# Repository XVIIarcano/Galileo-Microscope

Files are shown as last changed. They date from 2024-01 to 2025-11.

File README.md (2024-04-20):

# GALILEO Modular Microscope

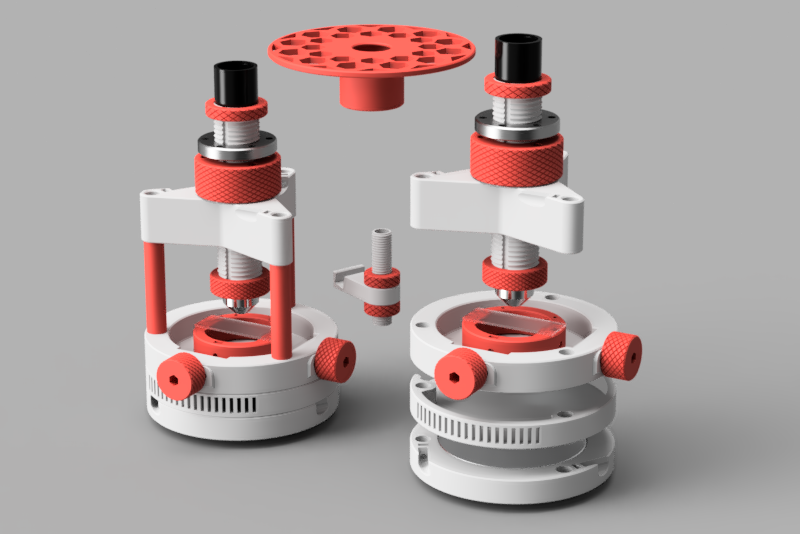
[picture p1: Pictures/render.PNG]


## Galiwhat?

This project is about an affordable, expandable and customizeable microscope based around basic hardware, 3d printing, and the few specific microscope components that cannot be worked around.
It started with a father without technical or academic knowledge whatsoever wanting to show micro-critters to his daughter, so the aim is fist and foremost to provide an enjoyable experience exploring small stuff for hobby or home use.

While Galileo is expandable, its core design prioritizes simplicity and affordability.  
I measure the success of this project on the fun you will have building it and using it, **especially** if it will be just a stepping stone for more advanced instruments and projects.

I hope to improve and expand on this project, and I would be thrilled to see other people picking up and modding it.
If you are looking for a DIY microscope already designed from the ground up to be a high end solution, with a vast selection of upgrades and configurations addressing a variety of scientific needs, have a look at the [PUMA project](https://github.com/TadPath/PUMA)

That said, it works, including the stage movement despite ample margins of improvement, and I hereby summon **The Ciliate Swarm Of Proof!**



Curious? Enthusiastic? Need to ~insult me~ _politely question my design choices_?
[**Join us on Discord**](https://discord.gg/2NHQUmsnHg)

## Basic modules

The main feature of this microscope is having each of the core functions carried out by a separate module, that exist independently and can be modded, customized and combined freely.
The basic configuration consists of the following modules and the [Printing and assembling](/Printing_and_assembling.md) file contains instructions and tips to put them together:

- **Base** 
- **Lighting (bring your own)** 
- **Stage** 
- **Standoffs**
- **Optical group** 
- **Phone holder (optional, but you will want to brag)** 

## Materials

The [BOM and components](/BOM_and_components.md) file contains a list of the necessary materials and some considerations about lenses and other accessories you will need.
I'll try to keep things synchronized but buy some extra nuts and screws ;) 

In general, you will need:

- M3 and M5 screws of different lenghts, and nuts to suit
- about 60 cm of 12 mm diameter pipe
- Some 3d printer spare parts like bed leveling springs and bowden tube.
- At least one objective, one eyepiece, and some other off the shelf microscope accessory

The objective is to keep the project lean and possibly cheap, your pricing may vary but for your reference the first functional prototype costed less than 80,00 Euros in hardware, plus the printed parts. 
Of course, if you want to bling it out you can, as with all things, but it would sort of miss the point.

## Modifications and accessories

The Mods folder is open to anyone who has something to contribute to the project.
Entries should be tested in real life, and include a readme file with any necessary information, instructions and bill of materials (don't take things for granted, remeber that this project is not meant for experts).

Simple variants, such as longer standoffs, or different tolerances on the optical tube thread, can be just generated from the CAD.
Please just notify me if you need them, I will generate them and add the STLs accordingly, no need to reinvent the wheel.

## Core specification
The core of the structure is formed by the three vertical rods of 12 mm diameter, in an equilateral triangle arrangement of 140 mm diameter (between the centers), with an external perimeter of another 10 mm all around, making the base module diameter 160 mm.
That's about it, there is no limit on how tall each "layer" should be, on the number of layers, nor on the lenght of the vertical rods, so if you have an idea for a particular lighitng setup, a finer stage module, or something else entirely, all you should do is fit it in a 160 mm diameter cylinder shape (minus the space for the rods).

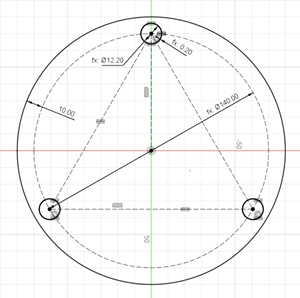
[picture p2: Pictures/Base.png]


## Wishlist and known issues

Below is a small list of things I would like to see, but have not been included in the core project (yet), if someone beats me to them, all the better!

- ~~Better movement, possibly with backlash compensation for the stage module~~ *(check the MODs folder!)*
- ~~Base alternative with some internal storage or some other solution to store stuff within the cylinder footprint when not in use~~ *(check the MODs folder!)*
- **NEW NO.1 PRIORITY** An advanced lighting module with its own light source and the possibility to mount a condenser and other amenities. *(There are some exciting developments! check the MODs folder and printables.com!)*
- ~~Fine focusing on the optical group, or a finer pitch option for the main focusing tube, or both!~~  *(check the MODs folder!)* 
- A better phone holder  

**Thanks to @MMutch on discord and @LarryD on Printables for working on their respective mods, and I hope this list can keep growing :)**

## Licensing

  
This work is licensed under a Creative Commons (4.0 International License)  
[Attribution—Noncommercial—Share Alike](https://creativecommons.org/licenses/by-nc-sa/4.0/)

## Thanks and acknowledgements

Thanks to Maff, who desinged the [Hadley telescope](https://www.printables.com/it/model/224383-astronomical-telescope-hadley-an-easy-assembly-hig) ([Metric version](https://www.printables.com/it/model/268580-hadley-telescope-official-metric-remix)).
Building and using a Hadley has been the inspiration that made me think this might be possible, and the design itself of the microscope is directly inspired by Hadley and the ecosystem of mods that grew around it.

> **Fun Fact**  
>_While I was looking for a name to this project, I found out that Italian scientist Galileo Galilei is credited with the idea of [reversing a telescope and using it as a microscope](https://en.wikipedia.org/wiki/Galileo_Galilei#Engineering), and that his first composite microscope design is [a vertical tube resting on three thin metal legs](https://catalogue.museogalileo.it/object/CompoundMicroscopeGalilean.html)... apparently the name had found me._ 

Thanks to the [Hadley discord community](https://discord.gg/DD3vHDNDjg), especially @Maff, @Baker and @Marci who encouraged me down this road after seeing the first render that was, at that point, still half a joke in my head.
They also pointed, and accompanied me, to the next chapter of my acknowledgements.

Thanks to the [Microscopy discord community](https://discord.gg/zGW95BwCy4), in particular @SmarmyNarwal and @Blekenbleu who explained many things to me without patronizing even if I was literally an incompetent barging in with ideas.
They helped me understand what I would be aiming for, what challenges I should prioritize, and how far the mark still is.

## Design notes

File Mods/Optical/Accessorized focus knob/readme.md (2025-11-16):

# Accessorized Focus Knob

_Brought to you by @Morpion on Discord and @XVIIarcano, but mostly Morpion_

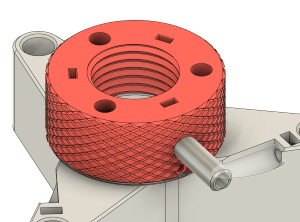
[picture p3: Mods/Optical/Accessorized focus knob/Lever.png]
/Mods/Optical/Accessorized focus knob/Lever.png

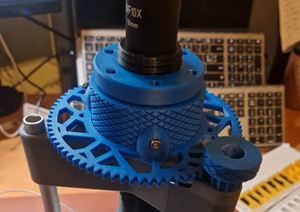
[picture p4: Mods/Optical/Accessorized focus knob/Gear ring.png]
/Mods/Optical/Accessorized focus knob/Gear ring.png


This modified knob and split ring allow the following:

- securing the knob with M3x6 screws instead of the glue 

- Attaching a lever to the knob for finer focus

- Attaching a gear ring, with a matching knob on any protruding vertical post for an even finer control

## Bill of Materials

- One set of printed parts, printed using the same settings as the rest of the microscope.

- 3x M3x6 SCHS screws for securing the knob to the split ring.
- 3x M3 nuts 
- 1x M3x30 SCHS screw for the lever.
- 3x M3x16 SHCS nuts for the gear ring.

## Assembling

- Thread the three M3x6 screws in the bottom holes around the perimeter of the knob, be gentle since you are threading on plastic. Do not tighten them all in yet.

- Drop M3 nuts in all three slots.

- Place the split ring in its seat on the spider, following the normal instructions for the anti backlash springs too.

- Position the nut and align the notches in the split ring with the screws.
Tighten the screws making sure they lock on the pockets on the split ring.
 
- Add the lever or the gear ring. 

>[!TIP]
>The rationale for the three nuts, even if you use only one lever, is that you may want to change the lever position based on where the focus point tends to fall for you, and taking the nuts out is not practical.

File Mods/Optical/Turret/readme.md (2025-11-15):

# Objective selection turret

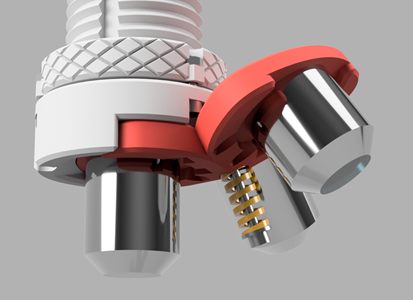
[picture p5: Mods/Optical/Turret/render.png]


This accessory replaces the standard single objective nut with a three positions rotating turret.
This way you can "zoom in" or "zoom out" selecting a different magnification objective. 

## Bill of Materials

- One set of printed parts, printed with the same settings as the rest of the microscope. You can replace the spring retainer with a simple washer, it is mostly just for show.

>[!TIP]
>Printing at a finer layer height can improve the rendering of the thread, and facilitate the assembling of the objective on the petals

- 6x M3x10 and M3 nuts (M3x12 will also work)

- 3x M3x12 SHCS screws and M3 nuts, (M3x16 will work as well, probably even M3x20 but if you go too long you start eating focuser travel)

- 1x M3x30 SHCS nut and M3 lock nut.

- 1x 8x20 mm spring (8x25 might work in combination with a longer screw)

## Assembling

Use one of your objectives to thread into the holes on the petals, then remove it, we will actually install the objectives later. The petals have RMS threads on them but it is unlikely that your printer can resolve them correctly, they will help guide the operation, but you will be actually threading the plastic with the metal of the objective. Do it nice and slow, and pay attention to go straight, and sand a bit the inner surface if needed. Take your time while the parts are disassembled, you do not want to struggle with this once the turret is on the microscope and you won't have ay leverage any more.

Assemble the rotor by joining the petals together with the M3x10 screws and nuts.

Slide the M3 lock nut in the slanted slot of the hub, note that it slides flat side down.

>[!TIP]
>The next steps are more comfortable if you remove the spider with the optical group from the microscope and keep it pointing upwards with the help of the smartphone support, just be careful not to scratch your eyepiece.

Add the gear nut to the bottom of the focusing tube, give it a couple of turns until it is out of the way.
Slide the hub in the slots of the focusing tube, careful, this will determine the orientation of the turret, I mounted mine pointing towards the bottom right, but you may prefer it pointing bottom left or even front, this is especially relevant if you also did the fine focusing lever mod, otherwise you can always just rotate the whole spider when you put it back.

When the hub teeth are level with the bottom of the optical tube, turn the ring nut back towards it, the holes on the ring nut and hub should align when there is a clearance of about 1 mm between the two.

Pass a screw trough each hole of the hub, then add the nuts in the ring nut, drawing them in until they reach the bottom of their seats, the 1 mm clearance  remains, and neither component is tilted.  
At this point the assembly is rigid, because the hub can't slide down any more, but the ring nut can't turn either.

Lean the rotor on the flat bottom of the hub, one petal flush with it.  Add the spring in the slot between the petals, and the M3x30 screw and spring retainer or washer.
Press the screw to compress the spring, then turn it to engage the lock nut and continue until it peeks out of the hole on the other side of the hub.  The locknut may have slided a bit in its seat, you can press and hold it up with a toothpick or something similar until the tip of the screw locks it in place.

Adjust the tension of the spring to your liking, it should be easy to turn, but also hold the rotor firmly enough in its three stable positions.

You can now add the objectives, and if you had removed and flipped the optical module, you can now reposition it on the microscope, checking that the objectives can rotate freely all around.
The space should be enoughto fit most objectives, but the longer ones may interfere with the thicker threaded standoff and smartphone holder or anything attached to it, so either may need to be reoriented.

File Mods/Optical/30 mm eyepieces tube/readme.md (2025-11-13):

_Originally published on printables.com by user @DaveSmith696_3620911, Discord идущийкреке_

# Description

I have redesigned the original tube (JIS), which is designed for 23.2mm eyepieces for 30mm eyepieces. The design is as simple as possible and can be modified to fit any other eyepiece, you just need to edit the CAD file to the desired size.

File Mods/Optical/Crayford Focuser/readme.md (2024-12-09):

_contributed by discord user MMutch_

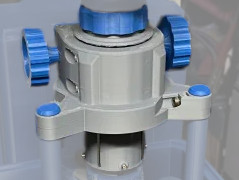
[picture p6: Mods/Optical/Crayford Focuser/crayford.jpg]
/Mods/Optical/Crayford Focuser/crayford.jpg


# Printing Instructions for the Crayford Focuser

Items marked with [a] are designated as accent, all others are primary colour.

** Print your chosen version parts I.E support vs non-support as there is a difference. **

All items have version that dont require any user added support, however there are some that ether have inbuilt removable supports or will need default slicer support adding which are only there for aesthetic reasons. Make sure that you print the corresponding parts (they are labelled in the naming structure) for example the Focuser_Body_x1 (Built in removable support).stl has a section that needs to be removed after printing where the Bearing_Block_x1 (Built in removable Support Version).stl is fitted, it should be easily removable and leave minimal signs it was there if printer/material used allows, and can be disposed of.

# BOM for Crayford Focuser

1 x Printed Parts (Body, Tube, Tube Adaptor, Eyepiece Adaptor, Bearing Block, Focus Knob, Eyepiece Locker)

3 x M5 Hex Nuts -- https://www.accu.co.uk/hexagon-nuts/7891-HPN-M5-A2

3 x M5x12 SHCS -- https://www.accu.co.uk/metric-cap-head-screws/3850-SSCF-M5-12-A2

7 x 4x3x5 Heat Set Inserts -- https://shop4fasteners.co.uk/heat-ultrasonic-threaded-inserts-brass-m3-x-5-74mm.html

7 x M3x8 SHCS -- https://www.accu.co.uk/metric-cap-head-screws/3818-SSCF-M3-8-A2

2 x M3x6 SHCS -- https://www.accu.co.uk/metric-cap-head-screws/3818-SSCF-M3-6-A2

4 x M4x20 SHCS -- https://www.accu.co.uk/metric-cap-head-screws/2830-SSC-M4-25-A2

4 x 'U' Groove 4mm x 13mm x 4mm Bearings -- https://www.amazon.co.uk/gp/product/B07V7Y1VVT/ref=ppx_yo_dt_b_search_asin_title?ie=UTF8&psc=1

1 x 110.5mm 5mm Diameter Rod (ideally Stainless steel) -- https://www.ebay.co.uk/itm/195740324799?var=495600341842&itmmeta=01HV152QP91T2EM5CFB4JQMK2A&hash=item2d930853bf:g:EbAAAOSwNFFkT~x-&itmprp=enc%3AAQAJAAAA4K%2FYtXpkaRDJxoHHHtXsM23rUVebpGkuCD9sKNMbcWPp2ZZtnkEyEJslF1Y1pCL8lxRWuFOp5TQeWT%2FXsEW4%2FUpJOw5JRbrEEODNTt2jmEa9xBe1TU9xw7Qkr7OIYFKRB4qNTfimhTiOVNK7SZk7nSfFjy3r7wZoyOf%2FKajt0uS%2FnA%2BgSC4DPSkfu%2Bp60ILHsD9mYTy%2BpDDvo%2B6V6%2FnoiL2UBgx0RtvYx8rIW7wRB%2FPS6MbpVLiF1RiyJpKAjHTR7LLsds3V4CiZFjyg8ELRTfVX8SIOEEQxq8l3zLxpU6Qy%7Ctkp%3ABFBMvPuKpdhj

2 x 16mm O/D 5mm I/D x 5mm Wide 625ZZ Bearing -- https://www.amazon.co.uk/625ZZ-Bearings-ABEC-5-Miniature-Bearing/dp/B08XLXJ6R6

2 x 109mm x 2mm Diameter Rod (ideally stainless steel) -- https://www.ebay.co.uk/itm/134173632090?itmmeta=01HV153Y9RNNQXWWSP9M3AW5Z5&hash=item1f3d5f265a:g:CSsAAOSwPc9WyGdN&itmprp=enc%3AAQAJAAAA4AygtEKGdGqWjNnNAfNLXD6kjoVY9hc1quTzC3Z7%2BIlZjWfuPSJIE8IB5LFQkUE9e4FW8ihKqvlguO6NXz8EogQujVqgYgnwSyHgwHNn8iO89YXgwOpvvCCRZDhBckjwDtcwv8xmX3V4vIzFf0%2FxNyO1piuIeUKu1ouL9RxfdqihmJRixidDZ5Qx%2FtpSkqFZ8Ae1lLsz3NLw4OVeLanNCZcGEyUbUdQRvABLeoiC95k%2B5l0AMHEaC7XXyjmuOxUKlZ06dhyhw1LMmuuJlkjScjdZCHnvAR7Xj5TuXd4wnnJS%7Ctkp%3ABFBMouWPpdhj

1 x 113mm x 10mm x 1mm Rubber Sheet -- https://www.amazon.co.uk/gp/product/B00MTW4VRA/ref=ppx_yo_dt_b_search_asin_title?ie=UTF8&psc=1

# Assembling

Body Assembly

Install the heat set inserts into the Focuser_Body_x1.stl (x4), then.

Put the 4x 'U' Groove bearings into the slots on the inside of the tube race in the Focuser_Body_x1.stl securing with the 4x M4x20 SHCS.

Focus Knob Assembly

Grind at least a 12mm flat side to the 110.5mm 5mm Diameter Rod on each end, then.

Fit one [a]_Focus_Knob_x2.stl to the 110.5mm 5mm Diameter Rod end using 1x M3x6 SHCS and slide on the 2x 16mm O/D 5mm I/D x 5mm Wide 625ZZ Bearings then fix the other [a]_Focus_Knob_x2.stl to the other end using the other M3x6 SHCS, then.

Fit the 2x 16mm O/D 5mm I/D x 5mm Wide 625ZZ Bearings with 110.5mm 5mm Diameter Rod and [a]_Focus_Knob_x2.stl into the Bearing_Block_x1.stl slots, then.

Align to the corresponding slots on the Focuser_Body_x1.stl (if using the No Support versions take not of the orientation by the direction arrow on the inside of the Bearing_Block_x1.stl) and using 4x M3x8 SHCS fix both assemblies together.

Tube Assembly

Glue (use CA glue i.e super glue) the 113mm x 10mm x 1mm Rubber Sheet to the 'flat' on the Tube_x1.stl and wait to dry, then.

Using an end of the 109mm x 2mm Diameter Rod shave off any plastic from the grooves in the Tube_x1.stl until the rods sit in the tube where the tube can smoothly without binding or any slop into the Focuser_Body_x1.stl making sure the 109mm x 2mm Diameter Rod sits in the groove of the 'U' Groove bearings, then.

Once fitting smoothly and correctly glue the rods onto the Tube_X1.stl (use CA glue i.e super glue) and wait till dry, then.

slide the Tube_x1.stl into the Focuser_Body_x1.stl

Tube to Thread Adaptor

Install the 3 x heat set inserts into the Tube_to_thread_adaptor_x1.stl, then.

Using 3 x M3x8 SHCS fix the Tube_to_thread_adaptor_x1.stl into the bottom of the Tube_x1.stl NOTE: this will lock the Tube_x1.stl into the Focuser_Body_x1.stl the screws will fit into the 3 slots on the bottom of the Focuser_Body_x1.stl when at full focus hight.

Eyepiece

Fit the stock spec eyepiece into the Eyepiece_Adaptor_x1.stl and place in the top of the Tube_x1.stl and then screw down the [a]_Eyepiece_Locker_x1.stl.

Crayford Focuser Complete

To fit to the Microscope use the stock hardware of 3 x M5x12 SHCS and 3 x M5 Hex Nuts however a modification to a tool is needed, cut down the short end of an Allen key where it fits into the head of the screw right at where the short end bends to the long end. The focuser body can be lifted to be level with the top of the stock length aluminium tubes to help with access to the samples and wont effect the function of the focuser, To which longer tube covers could be used to cover the exposed aluminium tube if desired. Also if desired there are [a]_Aluminium_Tube_Top_Caps_x3.stl's which are again purly cosmetic they have a 10.3mm O/D designed to fit 12mm O/D 11mm I/D aluminium tubes (they are a drop in fit) however if your tubes have a smalled I/D these will need sanding to fit.

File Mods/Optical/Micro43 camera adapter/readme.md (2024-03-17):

# Micro 4/3 camera adapter

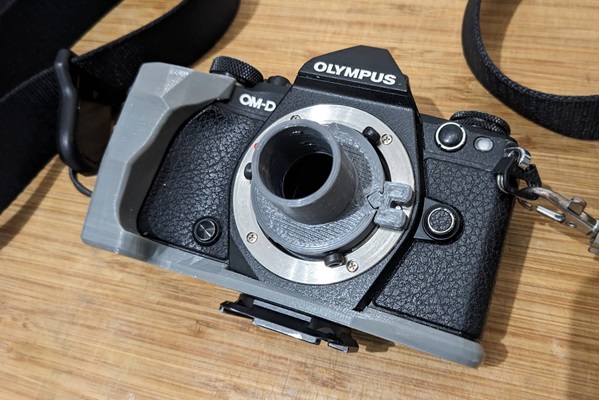
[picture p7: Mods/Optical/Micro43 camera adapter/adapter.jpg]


This adapter allows to attach a Micro 4/3 camera (tested with an OM-D E-M5 mkII) in place of the 23.2 mm eyepiece of the microscope.

For best results, enable the silent/electronic shutter with a 2 seconds delay, otherwise the kick of the mechanical shutter is enough to compromise the crispness of the image.

## Bill of Materials

- One set of printed parts, printed using the same settings as the rest of the microscope.
The block serves to latch on the lens release pin, and it is technically optional but it does help better securing the adapter.

>[!TIP]
>The fitting inside the camera body is intentionally tight, if you print it and it doesn't fit, you may have a hint of elephant foot, clean up the bottom with a deburring tool and/or sand it down a little bit.

- 3x M3x8 mm SHCS screws 

## Assembling

- Thread the three screws in the holes around the perimeter of the adapter.
Be careful as you are threading in plastic, you can stop 1 mm before the head of the screw bottoms out. 

- Push the block down in the square slot, with the flatter side of the prongs facing towards the lips of the flange, press until the top of the square plug is flush with the top of the disk. You may need to cut and file it a bit, especially if you had a bit of elephant foot, but we are going for a permanent friction fit, so if it gets stuck all the better, as soon as it goes all the way down.

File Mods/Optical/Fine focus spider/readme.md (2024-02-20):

# Fine focusing spider

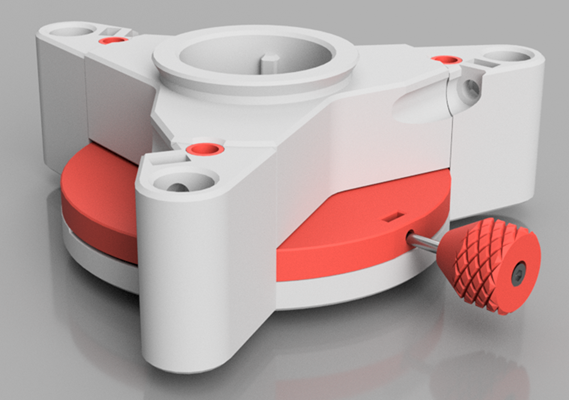
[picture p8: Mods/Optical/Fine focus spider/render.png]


This modified spider assembly allows a focuser movement of about 0.4 mm, moving the control lever over the span of about 75°.

Mechanically, this is achieved by sliding a disk with sloped surfaces in order to lift the entire main focuser mechanism by a small bit, while springs in the three corners keep the system under tension and prevent binding.  

You may also modify the CAD file to increase or decrease the slope and get a different movement range (again, within reason).  
Note that the 0.4 mm vertical movement is achieved out of the available travel of a 0.6 mm step sloping over 120°, so you may need to do some calculation to get the exact effective range you want from the 75° actual available movement.  
I also recommend adjusting in multiples of the layer height you are going to print with.

I pregenerated also a spider and rotor variant with a 1.0 mm step which should result in about 0.6 mm useful focusing range, that corresponds to 1/6th of a turn of the coarse focusing wheel using the default 3.8 mm pitch thread.   
If you do the math, you will see that we are talking about similar vertical travels over similar angles. but you may still prefer the lever control.    
I find for example that I can make smaller adjustments by grabbing the spider with the tip of my fingers and pushing forward the knob in the palm of my hand, and vice versa.

## Bill of Materials

**This mod only changes the spider of the standard focuser, please refer to the general BOM and instructions for the common parts, below is only what you will need specifically for this mod.**

- One set of printed parts, printed using the same settings as the rest of the microscope.
The "Paper Template" file is not really needed if all goes well, don't print it unless you have trouble with your PTFE tube.

- 3x 8x20 mm springs, same as those used in the standard focusing knob, but if you use longer ones they will just poke out, it may even get a steampunk vibe.

- 3x M3x40 mm SHCS screws and M3 nuts 

- 1x M3x50 mm SHCS screw, one M3 nut and optionally 1x M3 lock nut.    
>This is used as the lever shaft and can be replaced with one a bit shorter or longer. Experiment to taste considering also that you can adjust the final lever lenght by how much you will screw it in. The ideal screw is the one that sticks out the right amount for you after having bottomed out its seat in the rotor.

- 4mm diameter PTFE tube (bowden), about 55 cm for the basic version, 90 cm if you choose the PTFE lined nacelle.  
>I highlky recommend using plane cut in the slicer to print a test section of the spider, to verify the fit of your PTFE tube, if it doesn't you have a couple of options, jump to the bottom of this file.

- 3x M5x12 SHCS screws and nuts for locking the pipes (if you upgrade an existing spider you will recycle these).

>[!NOTE]
>The nacelle with PTFE groves may already improve the sliding of the disk, even if you don't actually add PTFE, as it would still have about 1/3 the contact surface.

## Assembling

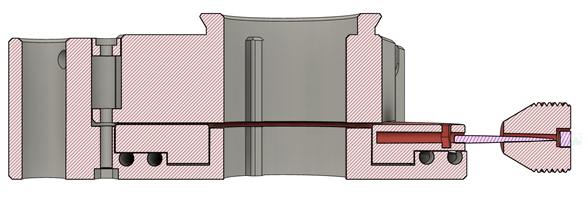
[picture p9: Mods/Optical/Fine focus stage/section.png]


- Remove the sacrificial layers from the three corners of the spider body, closing the nut slots in the bottom. Punch through them with an M3 screw and clear any burrs.

- Insert six spans of PTFE tube in the grooves of the spider body, they will provide an even slope instead of the inevitable "stairs" effect of the printed layers.   The tube should snap fit in the slot, push it one section at a time pressing down with the handle of a spoon going around the circle, cut off the excess when you get close to the end, cut as close as possible to the end of the groove, but avoid longer ends bumping and pushing out.

- Insert the M3 nut in the rotor (it goes in flat side down, unlike corner down as usual) and the M3x50 screw in the knob, then join them. As already mentioned the screw should bottom out in the pit which goes all the way trough the width of the rotor, but you can adjust it to taste or experiment with a different screw. You can also use an M3 locknut below the knob, to prevent it from sliding on the screw during use.

- If you have chosen the PTFE lined nacelle, this is the moment to insert the PTFE tubes in the bottom grooves.

- Apply grease to all mating surfaces, especially the central cylinder between rotor and spider, and the three vertical posts where nachelle and spider slide.  Place the rotor in the cradle of the spider body, followed by the nacelle. Make sure the rotor spins freely against both, and if in doubt add some grease, you can always clean up the excess once it is done.

>[!TIP]
>This is when you have to decide where you want the lever to point in relation to the microscope. Having it in front initially made sense to me but in practice I did not find it very comfortable, try placing it at the back right or back left depending on wether you are right handed or left handed, it is actually more natural as you keep your hands around the microscope, and you can control the movement by grabbing the spider and moveing the knob with the palm of your hand and vice versa.

- Drop the springs in the pits on the three corners, then the spring retainers. Use M3x40 and nuts the pits on the bottom of the spider to keep everything together. 

- Adjust the precharge of the springs, they must be just barely compressed, and they must press down evenly.  This means that unlike what appears in the render, the spring retainers may stick almost completely out, and the nut in the bottom may not engage for their full thread. If you have troubles finfing the sweetspot you may consider switching to M3x50 screws. Replacing the printed retainers with M3 washers will also shave a millimeter.      

- Proceed with the assembling of the other components and installation on the pipes, same as the standard optical module.

## PTFE whoes, and the paper trick

While putting together the prototype, I have found that the latest PTFE tube I bought was a bit larger and a bit stiffer than the one I got previously. It would not fit despite the grooves being the same dimensions as that on the bottom of the stage cart, and other projects in which the old pack of PTFE went just fine.  

Designing around all possible variations in PTFE quality is unfortunately a fool's errand, but I did make the grooves a bit more generous, since having some clearance would not be a dealbreaker in case you happen to have a smaller tube brand, while having the grooves too tight will be an issue.

If the PTFE tube you have on hand still does not fit, you have the following options.

1. Modify the CAD, there are two parameters PTFE_diameter and PTFE_poke that adjust the diameter and how much the tube rises out of the surface.

2. Try another brand, results are not guaranteed and it costs money, but it is an option.

3. The oven paper trick, weird but tested. Use the paper template file to print a donut shaped template, and use it to cut out some disks of oven paper. Stack them with some grease between spider and rotor in place of the PTFE tubes, experiment how much is enough, and how much is too much. While not ideal, oven paper does even out the printed layers and allow a smoother operation than just running the bare surfaces against each other.

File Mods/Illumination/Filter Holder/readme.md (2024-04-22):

_contributed by discord user MMutch_

This tray has a slot for standard 32 mm filters such as those available on Printables here:    
https://www.printables.com/it/model/788650-32mm-microscope-filters    
https://www.printables.com/it/model/167898-microscope-darkfield-filter-32mm    
https://www.printables.com/it/model/288750-microscope-filters

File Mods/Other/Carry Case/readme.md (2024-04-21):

_contributed by discord user MMutch_

# BOM for Carry Case

1 x Printed Parts (Base, Lid, Handle, Clips)

4 x 4x3x5 Heat Set Inserts -- https://shop4fasteners.co.uk/heat-ultrasonic-threaded-inserts-brass-m3-x-5-74mm.html

4 x M3x8 SHCS -- https://www.accu.co.uk/metric-cap-head-screws/3818-SSCF-M3-8-A2

8 x M3x30 SHCS -- https://www.accu.co.uk/metric-cap-head-screws/3818-SSCF-M3-30-A2

4 x Rubber Feet (25mm x 15mm) -- https://www.ebay.co.uk/itm/133359181553?itmmeta=01HV146RJWQ948JHB39W38KPR9&hash=item1f0cd39ef1:g:AvIAAOSwUtBjRZtq&itmprp=enc%3AAQAJAAAA4J%2FaLNfWOc3BAQ12J8P9rA3pkRGZKp1ZEXm%2FYW17OvQcGwrbzdUp9jF5NeVFmaMokFsankno6idKHbwFhG5jRMsBgvENQNQFjzV7H6iue7GSY%2F8qB3BHzD9ng4c9RjiWubMe5sBB3ophwQL3oMsIB7EFf%2FknG3xsD83HayFR%2B0quC6qYPHQTfUNtYyMq9T3v4Yt%2FyCrcDiUUSCmWRGp70heY1jJxVRUDHaetbFOHVTnZuqI1FqMOGGSHgBGcDeef6We5D0HuL2cNqpoHGIeAPWVrsfUFTxsNzfG00sPbjpAR%7Ctkp%3ABk9SR96Jm6TYYw

1 x Block of Foam (210mm x 210mm x 110mm)

# Carry Case Assembly

Fit the 4 x Rubber Feet (25mm x 15mm) to the Base_x1.stl, then.

Fit 4x M3x30 SHCS to the Base_x1.stl on the 4 sides (careful to not split the print)

Cut the Block of Foam (210mm x 210mm x 110mm) to the diameter of the microscope and fit into the base, then.

Instal the 4 x 4x3x5 Heat Set Inserts into the [a]_Handle_x1.stl, then.

Fit the [a]_Handle_x1.stl to the Lid_x1.stl using 4x M3x8 SHCS, then.

Fit the 4x [a]_Clip_x4.stl with the other 4x M3x30 SHCS to the 4 sides of the Lid_x1.stl.

Place Microscope into foam cutout and place lid over and secure with 4 side clips.

Carry Case complete.

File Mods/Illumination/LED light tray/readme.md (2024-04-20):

_Originally published on printables.com by user LarryD_

# Description

Designed this LED light to slide into the phone illumination module for the GALILEO Modular Microscope.  All of the parts were printed in Hatchbox PLA with the exception of the strain relief grommet which is PETG.  Note that the grommet will not fit unless it is printed at 69% in the X,Y directions and 100% Z direction.  I tried to make the changes in the grommet CAD file but it blows up when reduced that far.

The slide switch is wired to change between the TOP light and the BOTTOM light.  The LEDs in the parts list include a cable for USB charger and can be dimmed by holding the on/off button. 

When tightening the screws for the TOP arm tighten just enough to prevent unwanted movement so it can be repositioned easily.

I think the rest can be seen in the photos.

Parts List:

Slide Switch   
LEDs  
Double Sided Clear VHB Tape  
22 AWG Wire  
(3) M3 x 22 SHCS (for TOP Light Arm)  
(3) M3  StopNuts  
(2) M3 x 12 SHCS (for switch)  
(2) M3 Nuts  
Small Piece of plastic milk carton cut to fit opening over BOTTOM LEDs as diffuser

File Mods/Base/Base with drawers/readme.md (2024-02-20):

# Base with drawers

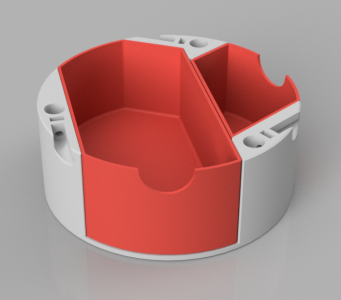
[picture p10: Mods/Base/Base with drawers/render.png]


## Bill of Materials

**This mod only replaces the design of the base module adding some internal space, screws for the rubber feet and for locking the pipes are unchanged from the standard version.**

- One set of printed parts, printed using the same settings as the rest of the microscope.  
There is an option for either the normal drawers with slots in the bottom for magnets, or simpler darwers to just print in vase mode.  

>You can use the "storage_height" parameter in the CAD file to adjust to taste, I pre-generated 60 mm and 30 mm versions. The 60 mm version is best for storing objectives, 30 mm is enough for a pack f slides, and other small items.
>There are "magnet_diameter" and "magnet_thickness" parameters as well if you happen to have a different magnet size at hand (if they are thicker than 3mm, you should also offset the bottom or you will poke a hole in it).    

- 2-6 3x8 mm magnets, each drawer has slots for 1 to 3 magnets, use as many as you prefer.  

- super glue  

## Assembling

Nothing to see here, just glue the magnets in place, add the M3 nuts for the rubber feet, slide in the rods, and secure them with the screws as for the standard base module.

>The only caveat I can think of, is that wehre on the standard base you could use longer screws for the rubber feet, and at worst you would have to cut a dent in the cover to make it fit, here a longer screw will interfere with the drawers.  
>If the correct screws are not available, you will have to cut them short or space them from below with washers or 3d printing a small buffer disk.

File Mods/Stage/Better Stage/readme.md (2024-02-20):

# Better Stage

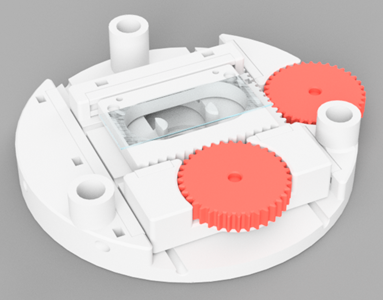
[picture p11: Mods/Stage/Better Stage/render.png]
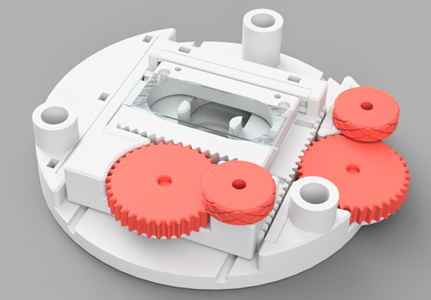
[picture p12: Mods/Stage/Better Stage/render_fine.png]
 

This mod addresses some major useability downsides with the dual M5 screw movement of the standard module.
The independent rack and pinion movement for x and y prevents the binding issue of the two interconnected knobs, and the new gears incorporate springs in order to eliminate backlash and shake inherent with the design of the basic module.

Despite being more complex, it is also easier to assemble and maintain.

> There is a basic version and a variant with fine movement knobs, if in doubt, print the latter, there is always time to remove the fine movement knobs if you change your mind, and replace them with the blank plugs which are also provided, going the other way wastes a lot of plastic.

## Bill of Materials

**This mod replaces the entire stage module, you will be able to recover only the clips and screws of the stage, therefore they are not listed in the BOM, and you may be able to recylce the PTFE tube if you can cut it and use it for the short backers without it bending out of shape**

**All screws mentioned are of the SHCS type**

- One set of printed parts, printed using the same settings as the rest of the microscope.  

- 7x M3 locknuts.

- 5x M3x10 for adjusting the rails 
> M3x12 or longer will also work, they will just stick out a bit more

- 2x M3x16 for holding the knobs

- 2x M3x20 and another 2x M3 locknuts if you use the fine movement variant.

- about 70 cm of PTFE tube

- 6x 8x20 bed leveling springs 
>unlike the anti backlash on the focuser knob, in this case 8x25 will not work
  
- super glue  

## Assembling

Remove the sacrificial layers from the following components, poking trough them with an M3 screw, and paying attention to remove any burr.

- module 
- lower plate 
- Upper half of the knobs
- Fine kobs 

Insert PTFE in all the pieces with a slot for it.  
The slots in the module and upper plate are open on the ends, meaning that the PTFE will tend to slide out, after you test fitted and cut to measure, add a few drops of superglue in the slots and press the ptfe on it so it will not budge.

Add the M3 locknuts in the slots on the module and lower plate, and M3x10 or M3x12 screws, but to not tighten them yet, give them just a couple of turns so that neither the screws nor the nuts can fall out. 

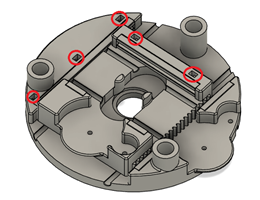
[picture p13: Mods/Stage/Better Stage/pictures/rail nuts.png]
 

Assemble the knobs by placing springs in the slots of the lower half, then leaning the upper half on it, and with the help of any flat tool (I used the back of a knife, but be safe) compress the springs so that they snap in the upper slots too.
The spring pressure should be enough to keep the two sides together. If you have troubles keeping the wheels aligned while you compress the springs, you can pass the M3x16 screw in them and a temporary M3 nut. 

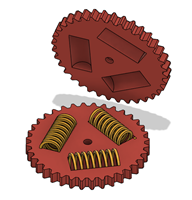
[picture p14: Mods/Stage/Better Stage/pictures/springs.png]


Prepare the upper plate by adding 2 M3x8 screws in the large holes, thread them in the plastic, until the head pokes out by a bit less than 1 mm, these will serve as stoppers for the slides, so they must be about the same height but not taller.
Install also the clips using the M3 screws and nuts that should be included with them.

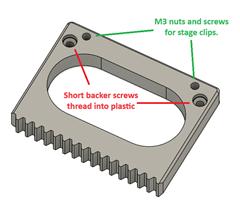
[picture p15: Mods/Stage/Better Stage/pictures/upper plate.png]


Insert the backers in the module and upper plate, they should snap fit and will be held in place by the plates, if they are loose, you can use a tiny bit of paper to shim them.
They must be level with the rack on the lower and upper plates to prevent it from tilting as the wheel moves past the centerpoint.
If you need to shim them, you should pay attention that they don't stick out too much that the wheel can't engage, nor too little that the plates can tilt.

Insert the rail in the back of the lower plate, followed by the upper plate which should slide in place freely.

Insert the lower knob in the module, aligning the teeth with the rack on the upper plate.
Secure it with the locknut on the bottom of the lower plate and the M3x16 screw.
You may add some grease on the bottom of the knob, but do not grease the teeth especially if you will use the fine focusing version, or you will get greasy fingers when you turn it. 

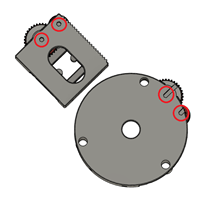
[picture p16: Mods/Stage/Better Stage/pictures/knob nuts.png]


Now it is time to tighten the screws on the back of the rail.
Start by tightening them equally until they are in contact with the rail, then by another couple of turns.
Test the sliding of the upper plate, it must move freely but with zero wobble.
Tighten and let go the screws, and the screw holding the knob, until you are happy with the results.

> [!IMPORTANT]
> Look at the plate movement from the side too, a consequence of the anti backlash split of the knobs is that the plate may tend to pull up on one side. 
> The compression applied by the screws prevents this too, and I found that the best result is achieved by keeping the side which pulls up a bit tighter than the other.

If you are assembling the fine movement version, install now the fine movement knob using the M3x20 and M3 locknut. 

>You may notice that there is a spot where the knobs and rack system runs more or less smooth due to imperfections of the print and alignment. The rack will not use one full turn of either of the knobs, so there is no harm in trying different orientations to look for the "alignment of the sweetspots".  

Install the backers and rail in the module body, folowed by the lower plate and knobs, with the same procedure and cares used for the previous stage.

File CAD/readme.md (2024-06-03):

# CAD files and resources

This folder collects useful files for the Galileo design, including the main source files for the "vanilla"  version of Galileo and a couple more, to make it easier to reference dimensions, generate derivatives, and multiple variants of certian components...

A special thanks goes to @roovian on discord for coding the [OpenSCAD file that generates standoffs with serial numbers on them](https://github.com/XVIIarcano/Galileo-Microscope/blob/main/CAD/Serial%20standoff%20generator.scad).
Use of that file is subject to the rules of the game as per the serial related channels on discord, if ou just grab it and print it, that's called cheating :P

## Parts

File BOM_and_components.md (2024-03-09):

# Bill of materials and microscope components

>[!CAUTION]
>This documentation is written by me, a salesman of totally unrelated goods with a degree in Political Sciences.  I write based on my personal experience, opinions, expectations and whatever I could understand from doing my own research.  
Some skilled and awesome pioneers have already completed their own builds with good results but...  

>**...Do your own research too before committing money to this project, no refunds.**

## 3d printed parts

Please read the [Printing and assembling](/Printing_and_assembling.md) file, there are a couple variants to choose from, and some tips about printing, so read it all at least once before you start pushing plastic.

For the sake of the shopping list, one spool of either PLA or PETG (ABS+ has been succesfully used as well) should be enough to complete the project, but printing all in one color the result may look boring, I suggest a two color scheme (one for the structure and another one for the gears and knobs), plus there are the optional TPU feet. 

The only caveat about color selection is that technically the inside of the optical tube should be matte black to avoid bouncing light around, which would cause a halo effect in the view, different colors and conditions may affect the results, but as a measure of caution stay away from canary yellow and glow in the dark filaments.

## Hardware

### Generic hardware

- 3x 20 cm aluminum pipes spans, 12 mm diameter.  
Wood or other materials would also work, as long as the material is rigid and the diameter is correct.

- 6x M5x12 SHCS screws and nuts for locking the pipes

- 2x M5x80 hexagon head bolts, 2x M5 lock nuts and 4x M5 washers for the stage movement.  You can also use M5 threaded rod 90 mm length instead of the bolts, but you will need 2 more locknuts and 2x M5 cap nuts, having done it, I do not recommend it.

- 3x M3x30 SHCS screws and M3 nuts for the anti backlash ring

- 2x M3x12 or M3x8 SHCS screws for the slide backers

- 3x M3x8 SHCS screws and M3 nuts for the TPU feet (optional)

- Superlube grease or similar, oil may or may not work, I think grease is better and easier to manage, you will have to glue parts next to greased surfaces, so it would be better if it doesn't spill.

- Superglue, there is debate on wether cyanaclrilate sticks to PETG, experiment if needed, but it is not dramatic if it fails.

- A bit of oven paper or similar, or a 25 mm diameter disk of 3 mm frosted acrylic if you are feeling dapper. This will cover the hole between stage and illumination.

### 3D printing related hardware

- PTFE tube (Bowden), 4 mm diameter, about 22 cm (optional, but used to allow the stage to slide around better), it will be finnicky to place it afterwards so I do recommend installing it from the start.

- 3x 8x20 mm bed leveling springs, the generic yellow ones.  
These also exist in 25 mm version, they may work as well, just precharge the anti backlash ring one less turn, it will eat 5 mm of travel to your focuser, wether this is a problem depends on your objectives, I don't have data to tell. 
Do note that if your springs remain 5 mm longer, you will also need M3x35 screws instead of M3x30.

### Microscope specific hardware

- at least one objective, with standard RMS thread, if in doubt start with a 4x one

- at least one eyepiece, 23.2 mm tube diameter (careful, 30 mm tubes exist), if in doubt start with a 10x eyeglasses friendly

- a pair of stage clips, the standard type which comes with M3 screws for installation  

- a pack of slides and cover slips

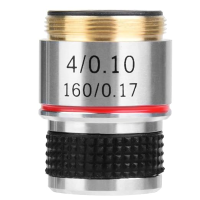
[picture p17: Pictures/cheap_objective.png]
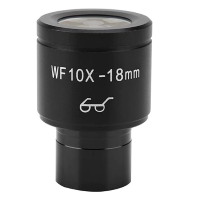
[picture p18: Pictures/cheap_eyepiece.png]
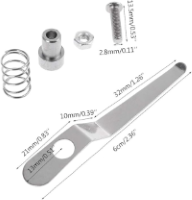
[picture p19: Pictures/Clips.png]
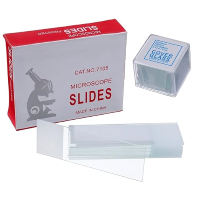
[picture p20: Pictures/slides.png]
     
_These are not intrinsecally good, just what I started with, and worked, that said here are the amazon links for the very same I used (Amazon Italy tho')..._

[Objective](https://www.amazon.it/dellobiettivo-obiettivi-acromatici-microscopio-biologico/dp/B07XRMMBRK/ref=sr_1_1_sspa?__mk_it_IT=%C3%85M%C3%85%C5%BD%C3%95%C3%91&crid=2NY08BKFBANIX&keywords=microscopio+lente+4x&qid=1706975572&s=industrial&sprefix=microscopio+lente+4%2Cindustrial%2C176&sr=1-1-spons&sp_csd=d2lkZ2V0TmFtZT1zcF9hdGY&psc=1)
[Eyepiece](https://www.amazon.it/Oculare-microscopio-WF002-G-grandangolare-regolabile/dp/B07NMLYC6X?pd_rd_w=Eui6O&content-id=amzn1.sym.96d1abda-aa11-4f46-aefd-d454143536ea&pf_rd_p=96d1abda-aa11-4f46-aefd-d454143536ea&pf_rd_r=RD4ZGR5EZV3XMWFMR19E&pd_rd_wg=lnUyw&pd_rd_r=a92d7860-4b5e-419b-b774-faf18eb14be3&pd_rd_i=B07NMLYC6X&psc=1&ref_=pd_bap_d_grid_rp_0_1_ec_ppx_yo2ov_dt_b_bia_item_t)
[Clips](https://www.amazon.it/unknows-portacampionatore-sconosciuti-Inossidabile-Applicazioni/dp/B0987PYLYM/ref=sr_1_4?__mk_it_IT=%C3%85M%C3%85%C5%BD%C3%95%C3%91&crid=EGTPWBC62ILR&keywords=clip+microscopio&qid=1706975423&s=electronics&sprefix=clip+microscopio%2Celectronics%2C160&sr=1-4)
[Slides](https://www.amazon.it/Huarew-microscopio-pre-puliti-contagocce-plastica/dp/B08Y75VR5Y/ref=sr_1_2_sspa?keywords=vetrini+microscopio&qid=1706975855&sr=8-2-spons&sp_csd=d2lkZ2V0TmFtZT1zcF9hdGY&psc=1)

### Tools

- Allen keys matching the screw heads

- an open wrench matching the M5 lock nuts

- Metal saw for the aluminum tube

- having Sandpaper (or a dremel) around never hurts, but it should not be necessary. 

## Considerations about lenses

The microscope has been designed and tested around cheap optics from Amazon, using better components will definitely make a difference but if you are in doubt wether to commit money to this project, there is no shame in starting cheap like I did (self absolutory? You bet I would be!).  

Here is an example of what 25,00 Euros of glass can do already (4x objective 10x eyepiece, no brand off Amazon).

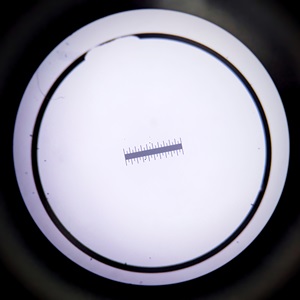
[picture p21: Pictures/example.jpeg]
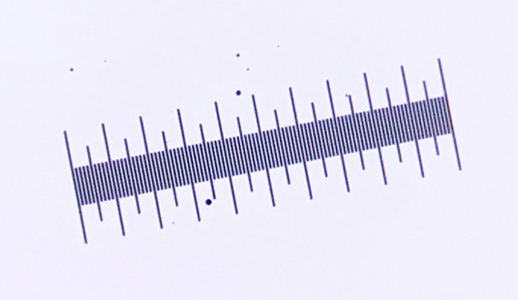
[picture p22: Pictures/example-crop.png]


The small notches are 0.01 mm, meaning that your average tardigrade would be as wide as the medium nothces.

The downside of these cheap lenses is that the optical design itself has some intrinsic shortcomings.

The focus plane is not straight, a phenomenon called field curvature, as a result if the center of the scene is in focus, the outes parts will not be, you may see something with the corner of your eye, and then have to move the stage and center it in order to get a good sharp view. 

They also lack any sophisticated optical coating, meaning that they will be more susceptible to things like chromatic aberrations (funny halos around bright and high contrast edges), and reflections.

That said, it is like using a cheap camera fom years past, it is not that the pictures didnt't turn out, just that they could have looked better, especially in challenging scenes, than newer or more expensive equipment.

If you want to know more about why certain lenses can come with a big price tag (and therefore what you can expect out of those which are cheap), I recommend you [this page on the Edmund Optics website](https://www.edmundoptics.com/knowledge-center/application-notes/microscopy/understanding-microscopes-and-objectives/).

If you are reading this, I'm afraid that like me we may not be their target customer, but their page is very comprehensive and informative none the less, if a bit technical. 

In my research, it has been the most useful, as they provide a detailed explanation of the nomenclature of microscope lenses. The various concepts they illustrate will be extremely useful when you have to do your shopping, so I wholehartedly recommend investing half an hour in reading their materials.

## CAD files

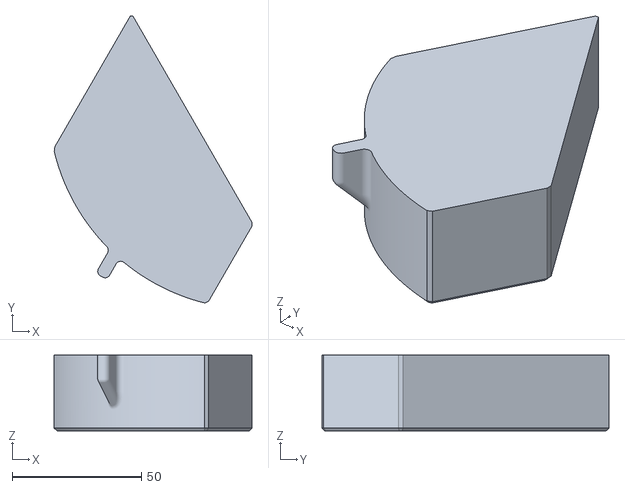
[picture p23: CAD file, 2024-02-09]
Mods/Base/Base with drawers/Box small vase 30.stl
76.3 x 110.9 x 29.2

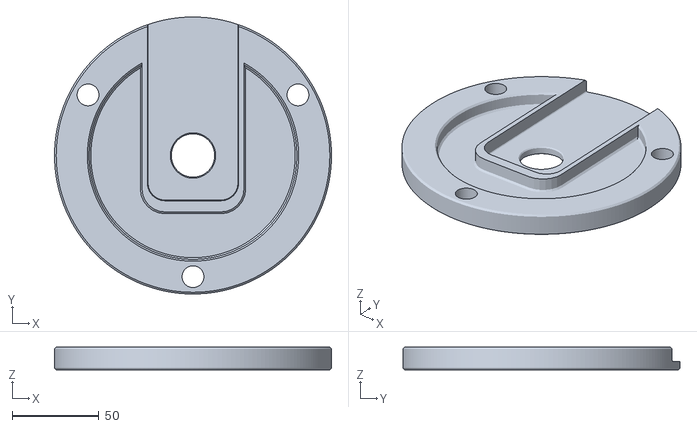
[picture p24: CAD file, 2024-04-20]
Mods/Illumination/Filter Holder/Filter_Slider_Body_x1.stl
160.0 x 160.0 x 13.2

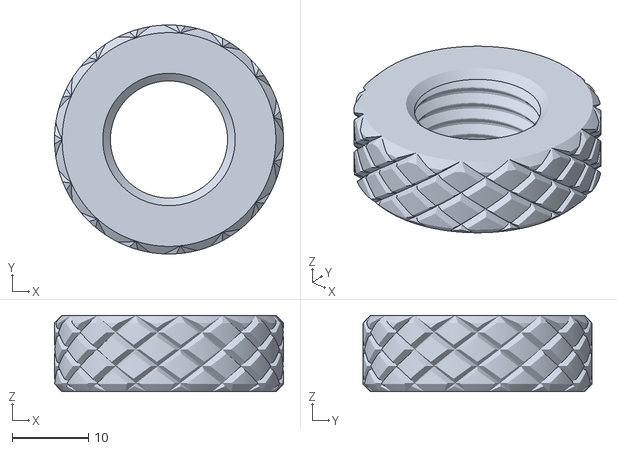
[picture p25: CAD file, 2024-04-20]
Mods/Illumination/LED light tray/Top standoff-accessory-ring.stl
30.0 x 30.0 x 10.0

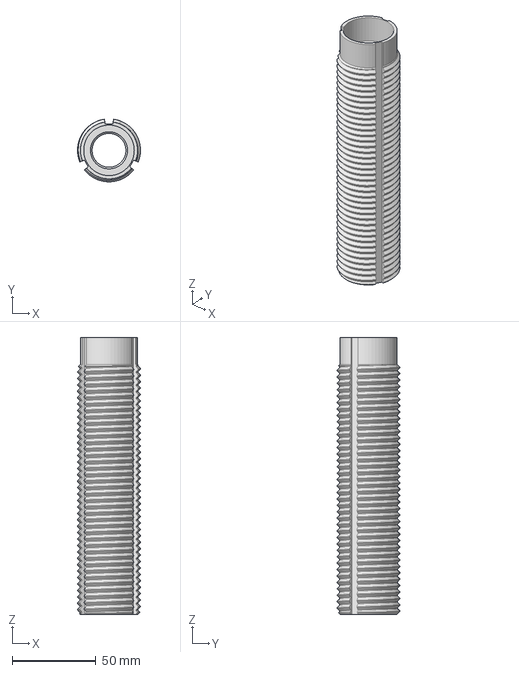
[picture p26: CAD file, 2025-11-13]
Mods/Optical/30 mm eyepieces tube/galileo-30mm-eyepiece-tube.step
37.5 x 37.3 x 165.0 mm

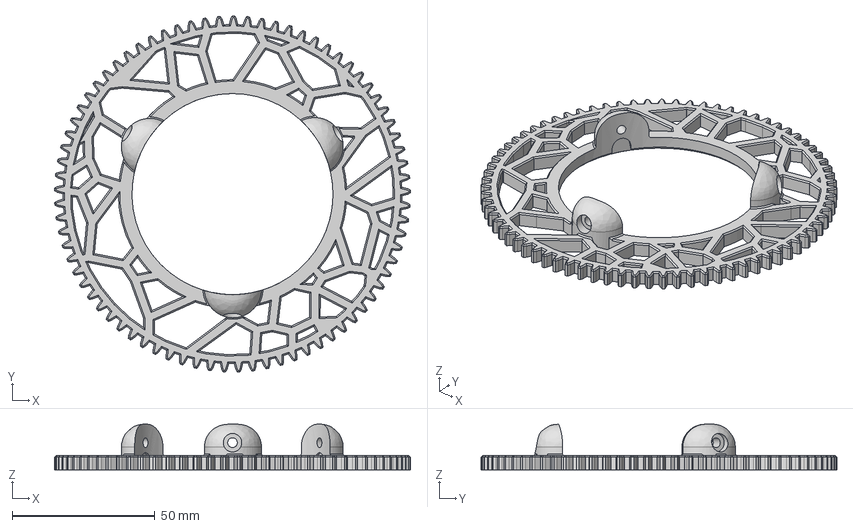
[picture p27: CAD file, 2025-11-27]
Mods/Optical/Accessorized focus knob/Fine focus wheel.step
124.6 x 124.6 x 16.0 mm

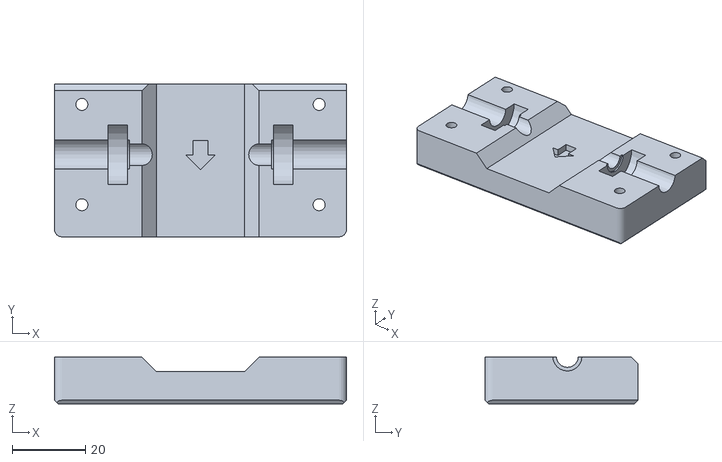
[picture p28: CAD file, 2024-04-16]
Mods/Optical/Crayford Focuser/Bearing_Block_x1 (No Support Version).stl
80.0 x 41.8 x 12.8

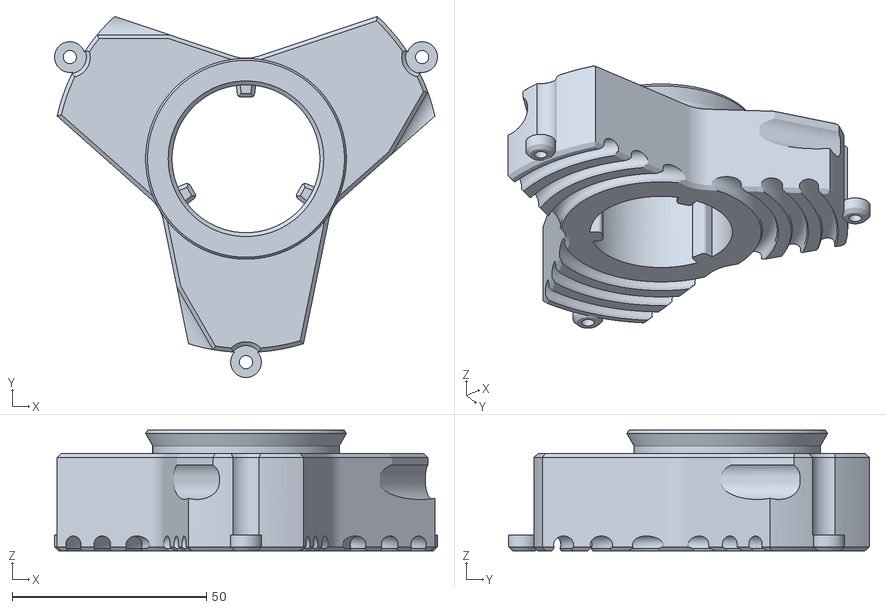
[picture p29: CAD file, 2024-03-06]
Mods/Optical/Fine focus spider/STL/Nacelle PTFE.stl
98.5 x 92.8 x 31.0

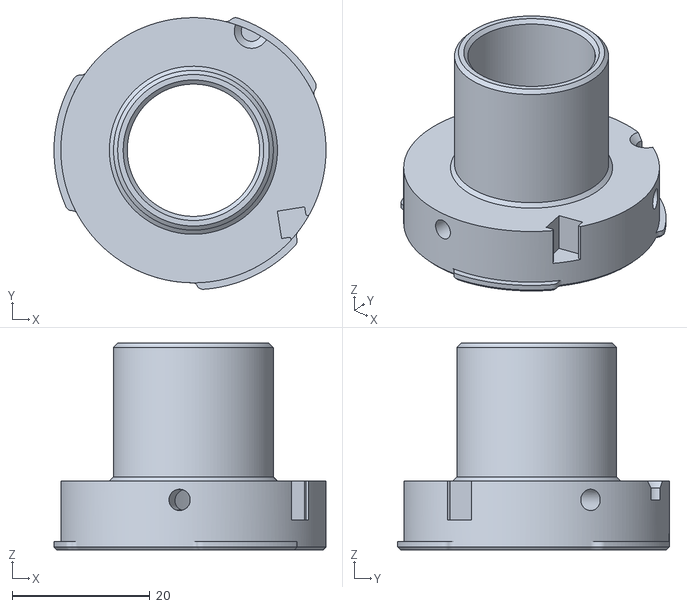
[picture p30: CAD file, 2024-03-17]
Mods/Optical/Micro43 camera adapter/M43 adapter.stl
39.5 x 39.4 x 30.0

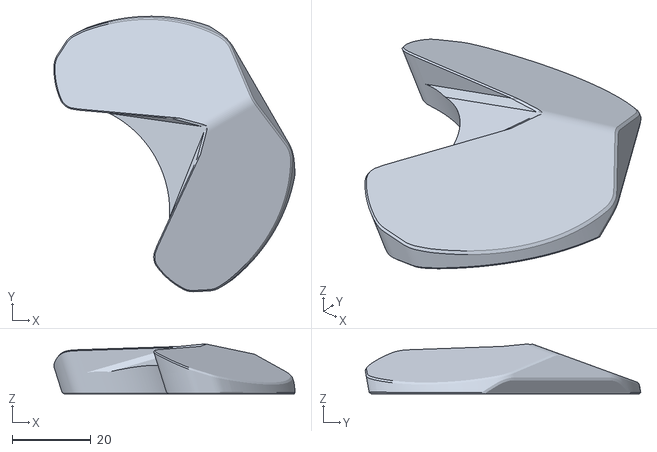
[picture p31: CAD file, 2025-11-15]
Mods/Optical/Turret/Turrett cover.stl
61.2 x 69.9 x 12.6

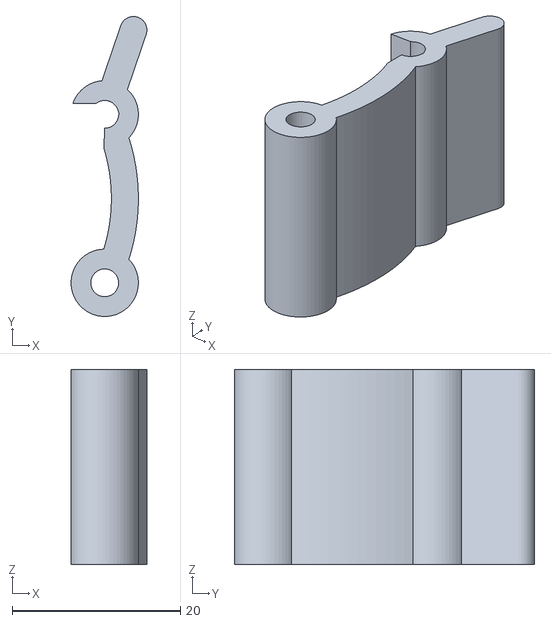
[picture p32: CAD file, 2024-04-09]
Mods/Other/Carry Case/[a]_Clip_x4.stl
9.01 x 35.6 x 23.2

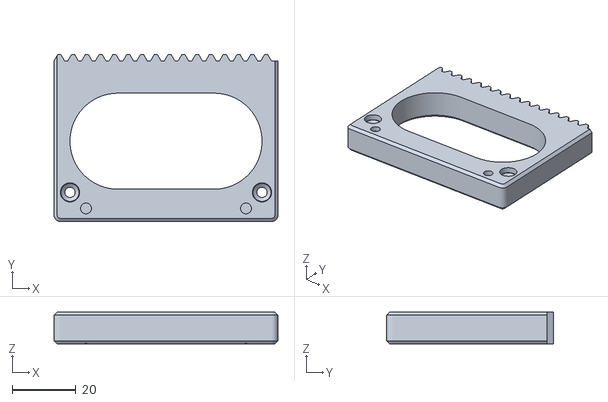
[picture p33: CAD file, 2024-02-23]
Mods/Stage/Better Stage/STL/Upper plate.stl
70.0 x 52.2 x 10.00

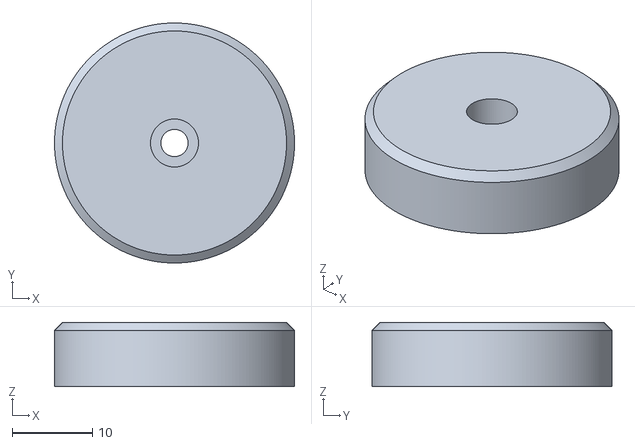
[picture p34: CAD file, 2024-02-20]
STL/Base/Pad (x3 - TPU).stl
30.0 x 30.0 x 8.00

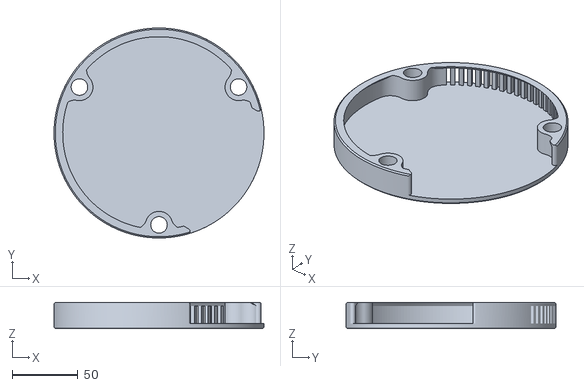
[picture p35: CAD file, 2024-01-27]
STL/Illumination/BYO Illumination Module.stl
160.0 x 160.0 x 20.0

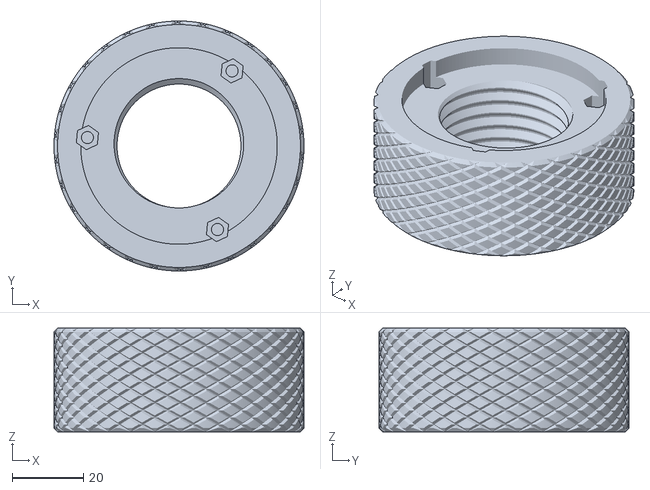
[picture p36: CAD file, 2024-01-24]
STL/Optical/4 mm pitch/Focus knob.stl
70.0 x 70.0 x 29.0

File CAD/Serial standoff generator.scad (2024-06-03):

Height = 80; // [80:Standard, 105:Crayford]
Text_Size = 5; //[1:8]
// Must be less than wall thickness
Emboss = 0.6; // [0.1:0.1:2]
// Assigned on Discord
Serial_Number = "0001";

/* [Hidden] */
$fn=50;
diameter = 12; // diameter of metal tube
wall = 2;
margin = 0.6; // allow for margin of error
radius = ((diameter + margin) / 2) + wall; // calculate desired outer radius
proportional_value = Text_Size / 2;
depth=5;

// Defaults
default_t = "text_on";
default_size = 4; // TODO - Can we make this 10?? To match internal size? There is an underlying value in text() -- This masks that.
default_font = "Liberation Mono";
default_spacing = 1; // Spacing between characters. There is an underlying value in text() -- This masks that. We try and match it here.
default_rotate = 0; // text rotation (clockwise)
default_center = true; //Text-centering
default_scale = [1,1,1];
default_extrusion_height = 2; //mm letter extrusion height
default_buffer_width = 0; //mm of buffer (thickening in all directions) to add to each letter
default_circle_ccw = false; // write on top or bottom in a ccw direction
default_circle_eastwest = 0;
default_cylinder_face = "side";
default_cylinder_updown = 0;

// Internal values - don't play with these :)
// This is much more accurate than the PI constant internal to Openscad.
internal_pi = 3.1415926535897932384626433832795028841971693993751058209;
internal_pi2 = internal_pi * 2;

// Internal values - You might want to play with these if you are using a proportional font
internal_space_fudge = 0.80; // Fudge for working out lengths (widths) of strings

debug = true;

// ---- Helper Functions ----
// String width (length from left to right or RTL) in OpenSCAD units
// NOTE: These are innacurate because we don't know the real spacing of the chars and so have to approximate
// They work for monospaced (fixed-width) fonts well
function width_of_text_char(size, spacing) = size * internal_space_fudge * spacing;
function width_of_text_string_num_length(length, size, spacing) = width_of_text_char(size, spacing) * length;
function width_of_text_string(t, size, spacing) = width_of_text_string_num_length(len(t), size, spacing);

//Angle that measures width of letters on perimeter of a circle (and sphere and cylinder)
function rotation_for_character(size, spacing, r, rotate = 0) = (width_of_text_char( size, spacing ) / (internal_pi2 * r)) * 360 * (1 - abs(rotate) / 90);

//Rotate according to rotate and if centred text also 1/2 width of text
function rotation_for_center_text_string_and_rotate(t, size, spacing,r,rotate,center) = ((center) ? (width_of_text_string(t, size, spacing) / 2 / (internal_pi2 * r) * 360) : 1) * (1 - abs(rotate) / 90);

module text_on_cylinder(
    t = default_t,                       
    locn_vec = [0, 0, 0],
    r,
    h,
    face = default_cylinder_face,
    updown = default_cylinder_updown,
    rotate = default_rotate,
    eastwest = default_circle_eastwest,
    ccw = default_circle_ccw,
    cylinder_center = false,
    extrusion_height = default_extrusion_height,
    center = default_center,
    font = undef,
    size = default_size,
    direction = undef,
    language = undef,
    script = undef,
    spacing = default_spacing
) 
{
    //Work on the side
    locn_offset_vec = (cylinder_center == true) ? [0, 0, 0] : [0, 0, h / 2]; 
    rotate(-1 * rotation_for_center_text_string_and_rotate(t, size, spacing, r, rotate, center), [0, 0, 1])
    translate(locn_vec + locn_offset_vec)
    __internal_text_on_cylinder_side(
        t,
        locn_vec,
        r = r,
        h = h,
        cylinder_center = cylinder_center,
        center = center,
        font = font,
        size = size,
        spacing = spacing,
        direction = direction,
        language = language,
        script = script,
        extrusion_height = extrusion_height,
        rotate = rotate,
        face = face,
        updown = updown,
        eastwest = eastwest
    );
}

module __internal_text_on_cylinder_side(
    t = default_t,
    locn_vec = [0, 0, 0],
    r,
    r1 = undef,
    r2 = undef,
    h,
    cylinder_center,
    extrusion_height = default_extrusion_height,
    center = undef,
    rotate = default_rotate,
    font = undef,
    size = default_size,
    direction = undef,
    language = undef,
    script = undef,
    spacing = default_spacing,
    buffer_width = default_buffer_width,
    updown = default_cylinder_updown,
    face = default_cylinder_face,
    eastwest = default_circle_eastwest
) 
{
    wid = width_of_text_char( size, spacing ); //TODO: refactor this out?

    function calc_radius_at_height_offset(r1, r2, h_total, h_offset) = r1 + ((r2 - r1) * (h_total - h_offset) / h_total);
    
    //Has to factor in up/downedness
    //Starts at middle height then height displacement is reduced under rotation and by the slope of the uneven radii
    function calc_height_offset_at_length(r1, r2, h, length, rotate, updown) = h / 2 - updown + length * rotate / 90 * cos(atan((r2 - r1) / h));

    function calc_radius_at_length(r1, r2, h, length, rotate, updown) = calc_radius_at_height_offset(r1, r2, h, calc_height_offset_at_length(r1, r2, h, length, rotate, updown));
    
    r1 = (r1 != undef) ? r1 : r;
    r2 = (r2 != undef) ? r2 : r;
    //NOTE: r is not used after here. We operate on generalised slanty cone (r1 and r2)
    
    //TODO: Look at changing this to extrusion_height_center
    //and renaming the other as text_center
    rr1 = (center) ? r1 - extrusion_height / 2 : r1;
    rr2 = (center) ? r2 - extrusion_height / 2 : r2;
    
    ccenter = (r != undef) ? center : false; //We don't do (text) centering for the slanty cones/helical paths (yet? ever?). Needs to do quite a few offset calcs.
    ddirection = ((r == undef) && ((direction == "ttb") || (direction == "btt"))) ? "ltr" : direction; //We don't do ttb or btt directions on slanty
    rtl_sign = (ddirection == "rtl") ? -1 : 1;

        //This code takes care of slanty cylinders and "normal" cylinders
    translate([0, 0, updown])
    rotate(eastwest, [0, 0, 1])
    for(l = [0 : len(t) - 1]) {
        //TODO: TTB and BTT need to have a different concept of path/length than this for RTL/LTR
           //width_of_... is half a char too long -- add 0.5 (counting from zero)
        length_to_center_of_char = width_of_text_string_num_length(l + 0.5, size, spacing);
        radius_here = calc_radius_at_length(rr1, rr2, h, length_to_center_of_char, rotate, updown);
        //Rotating into position and tangentially to surface -- Don't rotate per character for ttb/btt
        //-90 is to get centering at origin
        rotate_z_inner = -90 + rtl_sign * rotation_for_character(size, spacing, radius_here, rotate) * ((ddirection == "ttb" || ddirection== "btt") ?  0 : l);
        rotate(rotate_z_inner, [0, 0, 1]) {
            //Positioning - based on (somewhat innacurate) string length
            //Offset per character to go up/down the side in ttb/btt -- TTB down, BTT up
            vert_z_char_offset = (ddirection == "ttb" || ddirection == "btt") ?  (l * size * ((ddirection == "ttb") ? -1 : 1 )) :  0 ;
            //Only if RTL/LTR and if center -- center the text (starts off in a more visually appealing location)
            vert_z_half_text_offset_tmp = (len(t) -1) / 2 * (rotate / 90 * wid);
            vert_z_half_text_offset = ((ddirection == "ttb" || ddirection == "btt") || (ccenter == false)) ? 0 : vert_z_half_text_offset_tmp;
            translate([ radius_here , 0, vert_z_char_offset - l * (rotate / 90 * wid) + vert_z_half_text_offset])

            //Flip to tangent on the sloping side (without respecting rotation impact on the tangent -- rotate seems a little off. TODO: Investigate).
            rotate(atan((rr2 - rr1) /h), [0, 1, 0])
            //Flip onto face of "normal" cylinder
            rotate(90, [1, 0, 0])
            rotate(90, [0, 1, 0])

            //Modify the offset of the baselined text to center
            translate([0, (ccenter) ? -size / 2 : 0, 0])
        
            text_extrude(t[l],
                    center = false,
                    rotate = rotate,
                    font = font,
                    size = size,
                    spacing = spacing,
                    direction = undef, //We don't pass direction ( misaligns inside text() ). TODO: Investigate why
                    language = language,
                    script = script,
                    halign = "center", //This can be relaxed eventually
                    valign = "baseline", //Need this to keep all letters on the same line (could also support top -- otherw will make
                    extrusion_height = extrusion_height,
                    buffer_width = buffer_width);
        }
    }
}
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

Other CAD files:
STL/Optical/Spider.stl
STL/Smartphone holder/Inserts/Insert 25.4 mm.stl
STL/Smartphone holder/Phone tray.stl
STL/Stage/Cart.stl
CAD/Basic Elements Generator v3.f3d
CAD/Smartphone inserts generator v4.f3d
CAD/Standoff with accessories v5.f3d
Mods/Base/Base with drawers/Base module 30.stl
Mods/Base/Base with drawers/Base module 60.stl
Mods/Base/Base with drawers/Box large 30.stl
Mods/Base/Base with drawers/Box large 60.stl
Mods/Base/Base with drawers/Box large vase 30.stl
Mods/Base/Base with drawers/Box large vase 60.stl
Mods/Base/Base with drawers/Box small 30.stl
Mods/Base/Base with drawers/Box small 60.stl
Mods/Base/Base with drawers/Box small vase 60.stl
Mods/Illumination/Filter Holder/[a]_Filter_Tray_x1.stl
Mods/Illumination/LED light tray/Bottom LED Lighting Module.stl
Mods/Illumination/LED light tray/Top LED Holder.stl
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

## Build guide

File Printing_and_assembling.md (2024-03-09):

# Printing and assembling

The following instructions cover the basic modules, over time some alternatives and mods may become available, so while the basic principles will still apply, it is always a good idea to check wether variants of the various modules have appeared, and how you may want to incorporate them in your build.

In particular your objective will need a specific focus tube lenghts, the DIN standard has a 160 mm tube, the JIS standard has a 170 mm tube. Choose yours accordingly and note that the threaded tube in the STLs are 5 mm shorter but that's correct, the objective holder nut adds the missing 5 mm.

>[!NOTE]
>The bill of materials and some considerations about lenses and other accessories can be found in the [BOM and components](/BOM_and_components.md) file. 

## Printing tips

### Materials

The microscope is not subject to heat (unless something goes horribly wrong with the lighting module or you put something reactive on the stage).

All prototyping has been done in PETG, the extra rigidity and general easier printing of PLA should only improve the results, ABS may be overkill but it has been tested succesfully(Esun ABS+ specifically, thanks discord @roo) and it did not introduce any unexpected tolerance issues due to shrinking, so I can remove the previous warning about it.

As mentioned in the [BOM and components](/BOM_and_components.md) file, prefer a matte black material for the optical tube for the best optical performance.

### Settings

Print with a 0.4 mm nozzle at 0.20 mm layer height.
I used these Settings succesfully for the parts with threads as well, but going lower for those cannot hurt if you feel like it.  

A high infill will add to the overall rigidity of the parts, prototyping and testing has been done with 4 walls and 40% gyroid infill, following the Voron recommended settings I already had a profile for. You can probably get away with less on the lower modules, while I would not skimp on the spider, as on any of the gears. 

The STLs are already oriented for printing without supports, but some items like the focus tube and the standoffs do require a brim ulness your bed adhesion is exceptional, so add it at your discretion.
The focus tube has a bevel at the extremities, it helps it not to bind towards the bottom of the objective nut, and it will soak up any imperfection as you clean up the brim, but using a deburring tool and doing a clean job is still a good idea.

>[!TIP] 
>Do a couple test prints.  
>Print the objective holder nut and a 40 mm section of the focusing tube using the plane cut function of your slicer to test the thread, a little stiff is ok (it will wear itself down and you will add some grease where it matters), hard binds on the other hand may be a showstopper.   
>Don't print all at once the parts with nut holes, you don't want to spend half a spool of plastic then discover that your hardware won't fit, the same applies to the pipe holes in the modules. The base module is a good place to start since it has the holes for the pipes, vertical M5 and horizontal M3 nut pits, so it already has a bit of everything.

## Assembling

Each module is assembled separatey, then you can simply stack them along the vertical rods and tighten the screws on the base and spider modules when you are done.
You can use one of the rods to "break in" the holes of each module beforehand, so that the stacking will be smoother.

**Unless otherwise noted, all screws are of the SHCS type.** 

### Base

- (Optional) Add the M3 nuts on the bottom, then use M3x8 screws to secure the three TPU feet.  

- (Optional) Fill the cover with something that can act as ballast, sand, fishing leads, shot...     
Glue the walls of the cover and reverse the base upside down on it, wait for the glue to set, then flip.  

- Slide in the aluminum rods, and secure them with the M5 nuts and M5x12 screws. 

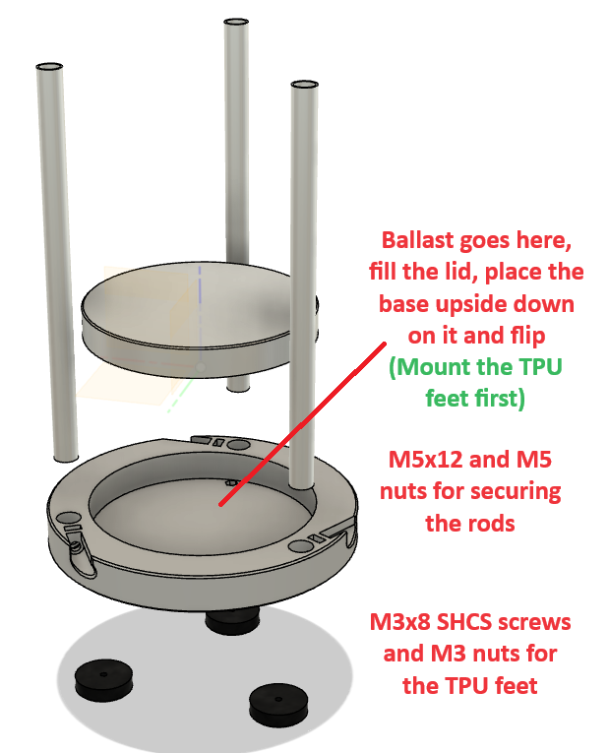
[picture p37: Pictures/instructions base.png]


### Lighting (bring your own)

Nothing to do here, just stack it in place.   
You will slide a cellphone here to provide the lighting, either with the torch or with a browser open on `about:blank`, which will give you a nice and dimmable white background.

Having this module open towards the front is handy, but it may bump against the stage movement knob, so you may consider rotating the module to open at the rear left instead.

### Stage

>[!NOTE]
>The stage module has integrated supports in the slits where the knob axles will travel, remove them and use an M5 screw to file the inside of the slits until it slides freely from one side to the other.

Add M5 nuts in the verticasl slots of the cart.

Add M3x8 screws in the large holes on the cart, thread them in the plastic, until the head pokes out by about 1 mm, these will serve as stoppers for the slides, so they must be about the same height but don't need to be taller.

Add the clips in the small holes, using the recesses for the nuts on the underside of the cart.

Insert a span of 4 mm PTFE tube in the slot on the underside of the cart, it will help it slide smoothly.   The tube should snap fit in the slot, push it one section at a time pressing down with a spoon going around the circle, cut off the excess when you get close to the end, cut as close as possible to get a seamless ring, but avoid the two ends bumping into each other and pushing out. 

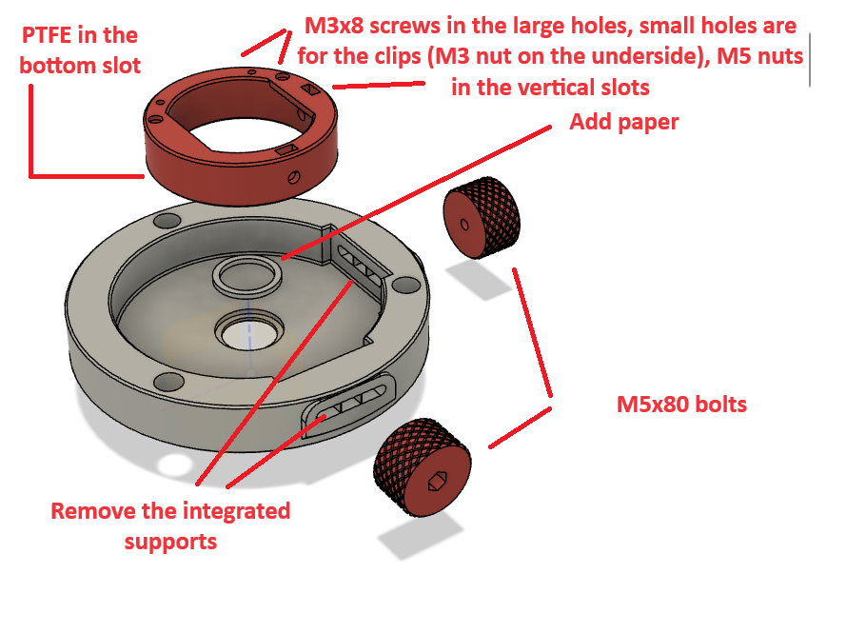
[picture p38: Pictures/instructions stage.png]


Insert an M5x80 hexagon head bolt in the knobs.  

Place the knobs with a washer on each side of the slit in the module body, then tighten a lock nut on the inside by holding it with a wrench as you turn the knob, as shown in the picture, it should be tight enough to hold the knobs in, but free to spin and slide side to side (as soon as you use it, you will get a feeling of how tight they should be - not much actually - and you can adjust to taste)

Towards the end of the knob insertion, align it with the nut in the cart, so that it will be pulled in.  Do not worry if the screw exits inside the cart by about 1 cm, even at low magnifications, it will remain well outside of the field of view and it won't cast a shadow.
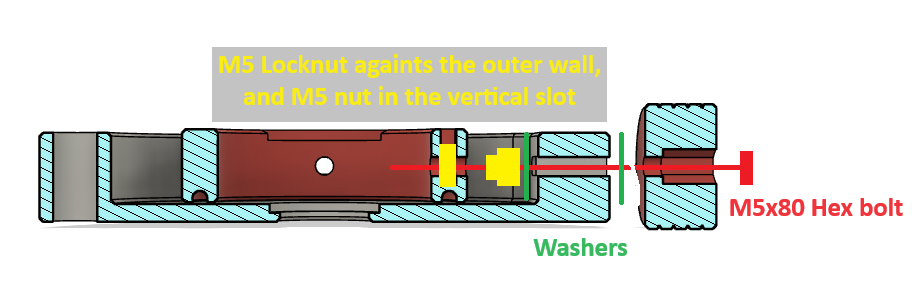
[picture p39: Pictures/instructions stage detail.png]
Pictures/instructions%20stage%20detail

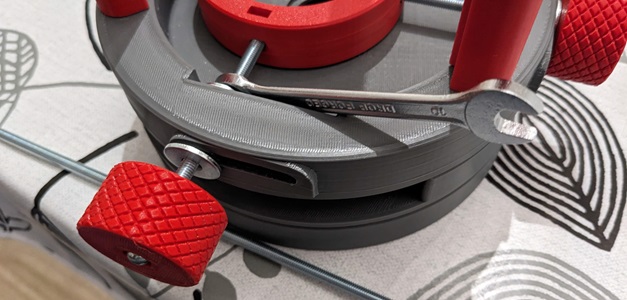
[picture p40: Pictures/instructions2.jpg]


>If you have trouble finidng the M5x80 bolts, you can use one locknut and one capnut at the end of the threaded rod in the knob, but it is not recommended as they will want to come loose while you tighten the other locknut.

Glue the diffuser ring to a sheet of oven paper, and cut out the excess, you can put this in the slot on the floor of the stage module to prevent wet samples from dripping in the illumination stage.
You can use a 3mm disk of acrylic if you have any around, it will do a much better job and look nicer too, but I would not go buy a sheet just for this.

### Standoffs

Not much to see here either, if you opt for the plain standoffs just slide them in place.
The default size of 80 mm should be a good starting point but you can cut them shorter or stretch them taller directly in the slicer.

There is also a threaded version with an accessory ring and a simple phone holder, which will allow you to use the phone as a reflected light source ("light from above" in plain english). 
You can use the accessory ring to rise or lower the phone along the shaft, or to clamp the holder down at the bottom, you can even add two rings one above and one below.

If your phone doesn't fit, or you wish to develop something else based on this, you can use the source file in the [CAD](/CAD) folder to edit as needed (this is true of the whole project by the way)

### Optical group

>[!NOTE]
>The focus knob has a sacrificial layer at the bottom of the spring wells to allow proper printing without supports. Punch trough them with an M3 screw, and make sure that all the burrs come off.

Assemble the objective in the objective holder, the nut has RMS threads on it but it is unlikely that your printer can resolve them correctly, they will help guide the operation, but you will be actually threading the plastic with the metal of the objective. Do it nice and slow, and pay attention to go straight. If you have more than one objective, it may be a good idea to just print multiple nuts and leave each objective on its own.

Test fit the eyepiece in  the optical tube, you can sand the inside or wrap some tape around the eyepiece shaft to adjust the fit (or modify the CAD...).

Apply a little bit of grease on the sloped sides of the collar of the spider, and insert the split ring on it.

Insert M3 nuts in the holes on the bottom side of the focusing knob, then slide it over the split ring (do this upside down, or the nuts will fall off!), the knob should compress the split ring and snap fit on it.
You should eventually glue the knob to the split ring, but donìt do it just yet, at the end of the assembling, after you check that all is ok, you can make this mating final by applying glue on the flat surface of the split ring and pressing he knob down (do not exagerate and be careful, you do not want any glue to end up between split ring and spider body and cause a jam).

Add some grease on the central and upper part of the optical tube, avoid greasing the extremity where the objective nut will be, it is ok if that is a bit stiffer, while all other rings have to turn as smooth as possible the nut has to stay in place.

Insert the tube in the spider from below, rotating the focusing knob as soon as it catches the threads on the tube so that you can draw it up. Be careful, the knob is not glued to the ring yet and there are no screws preventing the nuts inside from being dislodged if it lifts.

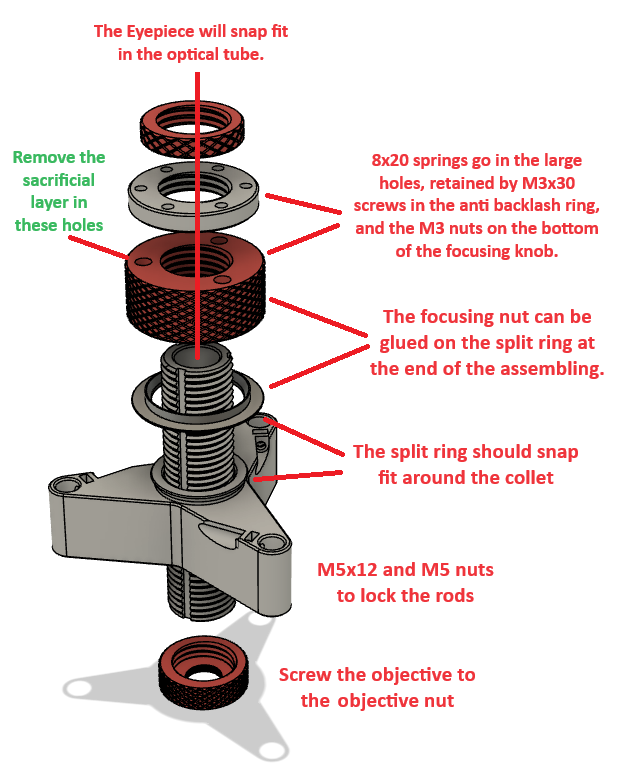
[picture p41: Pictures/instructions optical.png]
Pictures/instructions%20optical


Insert the springs in the holes on top of the knob, then add the anti backlash ring, tighten it down until it compresses the springs. A couple millimeters clearance should remain between the two rings, there are two sets of holes on the backlash ring so that you can adjust it in half a turn increments, you can change this later based on your preference.

Use M3x30 screws trough the backlash springs and down to the nuts in the focus ring to secure the assembly together, do not overtighten the screws, and make sure the backlash ring is not tilted.

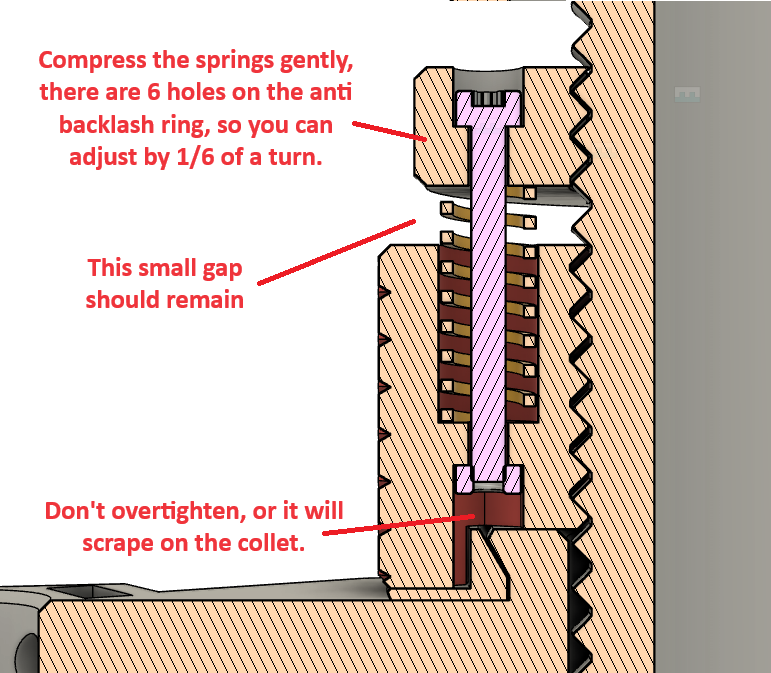
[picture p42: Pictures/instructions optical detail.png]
Pictures/instructions%20optical%20detail


Test the assembly a few times, any stiffness should break in soon as the surfaces wear a little and the grease spreads.
If you are happy with the results, you can now push the optical tube up, this will detach the focus knob from the split ring, but the nuts are now secure, so you can add the glue and press it back down.   

>[!TIP] 
>You do not really need to glue the knob down, the microscope is actually perfectly useable also with the knob just pressed together, in use, you may occasionally experience it pushing up, but it is no big deal, so you can take your time testing, adding (or cleaning off) grease, etc...

Add the accessory ring on the top of the focus tube, followed by the eyepiece, and the objective ring on the bottom.

You can now install the asembly on the lower part of the microscope.

### Phone holder

Print the main body, and an insert to suit the clearance between the body and your specific eyepiece, the insert just slides in, as you can have more than one for different eyepieces. Install the phone holder by sliding it on the eyepiece, and use the accessory ring on the optical tube to move the support higher or lower based on the eye-relief distance of your eyepiece. **Note that you may have to plane cut or extend the inserts to the length of your eyepiece as well** 

If your holder wobbles because none of the pre-generated sleeves fits right on your eyepiece, you can use the source file in the [CAD](/CAD) folder to generate a custom size.

This type of holder is handy because you just lean the phone on it but it may be too small for your phone, be careful.  
If your phone is too large, instead of printing some sort of larger dish you may prefer a different solution like [this one](https://www.printables.com/model/629333-ocular-phone-mount) or [this one](https://www.openocular.com/designs)

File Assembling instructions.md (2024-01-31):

# Printing and assembling

The following instructions cover the basic modules, over time some alternatives and mods may become available, so while the basic principles will still apply, it is always a good idea to check wether variants of the various modules have appeared, and how you may want to incorporate them in your build.

In particular your objective will need a specific focus tube lenghts, the DIN standard has a 160 mm tube, the JIS standard has a 170 mm tube. Choose yours accordingly and note that the threaded tube in the STLs are 5 mm shorter but that's correct, the objective holder nut adds the missing 5 mm.

## Printing tips

### Materials

The microscope is not subject to heat (unless something goes horribly wrong with the lighting module or you put something reactive on the stage.

All prototyping has been done in PETG, the extra rigidity and general easier printing of PLA should only improve the results, ABS may be both overkill and introduce some unexpected tolerance issues due to shrinking, I do not recommend it, but I may revise this paragraph if sufficient empyrical results emerge from people trying it none the less.

### Settings

Print with a 0.4 mm nozzle at 0.20 mm layer height.
I used these Settingssuccesfully for the parts with threads as well, but going lower for those cannot hurt if you feel like it.  

A high infill will add to the overall rigidity of the parts, prototyping and testing has been done with 4 walls and 40% infill, you can probably get away with less on the lower modules, but I would nt skimp on the spider, and on any of the gears. 

The STLs are already oriented for printing without supports, but some items like the focus tube and the standoffs do require a brim ulness your bed adhesion is exceptional, so you should add it at your discretion.
The focus tube has a bevel at the extremities, it helps it not to bind towards the bottom of the objective nut, and it will soak up any imperfection as you clena up the brim, but using a deburring tool and doing a clean job is still a good idea.

>[!TIP] 
>Do a couple test prints.  
>Print the objective holder nut and a 40 mm section of the focusing tube using the plane cut function of your slicer to test the thread, stiff is ok (it will wear itself down and you will add some grease where it matters), hard binds on the other hand may be a showstopper.   
>Don't print all at once the parts with nut holes, you don't want to spend half a spool of plastic then discover that your hardware won't fit, the same applies to the pipe holes in the modules. The base module is a good place to start since it has the holes for the pipes, vertical M5 and horizontal M3 nut pits, so you already have a bit of everything.

## Assembling

Each module is assembled separatey, then you can simply stack them along the vertical rods and tighten the screws on the base and spider modules.
You can use one of the rods to "break in" the holes of each module beforehand, so that the stacking will be smoother.

**Unless otherwise noted, all screws are of the SHCS type.** 

### Base

- (Optional) Add the M3 nuts on the bottom, then use M3x8 screws to secure the three TPU feet.  

- (Optional)Fill the cover with something that can act as ballast, sand, fishing leads, shot...     
Glue the walls of the cover and reverse the base upside down on it, wait for the glue to stick, then flip.  

- Slot in the aluminum rods, and secure them with the M5 nuts and M5x12 screws. 

### Lighting (bring your own)

Nothing to do here, just stack it in place.   
You will slide a cellphone here to provide the lighting, either with the torch or with a browser open on `about:blank` to have a dimmable white background.

### Stage

>[!NOTE]
>The stage module has integrated supports in the slits where the knobs will travel, remove them and use an M5 screw to file the inside of the slits until it passes freely and slides freely across.

Add M5 nuts in the verticasl slots of the cart.

Add M3x8 screws in the large holes on the cart, thread them in the plastic, until the head pokes out by a bit less than 1 mm, these will serve as stoppers for the slides, so they must be about the same height but not poke above them.

Add the clips in the small holes, using the recesses for the nuts on the underside of the cart.

Insert a span of 4 mm PTFE tube in the slot on the underside of the cart, it will help it slide smoothly.   The tube should snap fit in the slot, push it one section at a time pressing down with a spoon going around the circle, cut off the excess when you get close to the end, cut as close as possible to get a seamless ring, and at a slight angle to prevent any pointy edge from poking out. 

Insert an M5x80 hexagon head bolt in the knobs, or use one locknut and one capnut as shown in the photo.

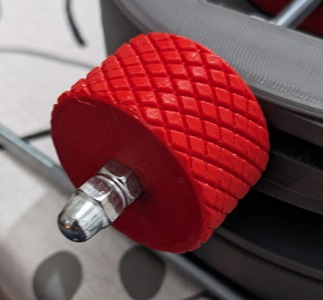
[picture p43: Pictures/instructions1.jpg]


Place the knobs with a washer on each side of the slit in the module body, then tighten a lock nut on the inside by holding it with a wrench as you turn the knob, as shown in the picture, it should be tight enough to hold the knobs in, but free to slide.



Towards the end of the knob insertion, align it with the nut in the cart, so that it will be pulled in.  Do not worry if the screw exits inside the cart by about 1 cm, even at los magnifications, it will remain well outside of the field of view and it won't cast a shadow.

Glue the diffuser ring to a sheet of oven paper, and cut out the excess, you can put this in the slot on the floowr of the stage module to prevent wet samples from dripping in the illumination stage.
You can use a 3mm disk of acrylic if you have any around, it will do a much better job and be nicer too, but I would not go buy some just for this.

### Standoffs

Not much to see here either, if you opt for the plain standoffs just slide them in place.
The default size of 80 mm should be a good starting point but you can cut them shorter or stretch them taller directly in the slicer.

There is also a threaded version with an accessory ring and a simple phone holder, which will allow you to use the phone flashlight as reflected light source ("light from above" in plain english). 
You can use the accessory ring to rise or lower the phone along the shaft, or to clamp the holder down at the bottom.

If your phone doesn't fit, or you wish to develop something else based on this, you can use the source file in the [CAD](/CAD) folder to edit as needed.

### Optical group

>[!NOTE]
>The focus knob has a sacrificial layer at the bottom of the spring wells to allow proper printing without supports. Punch trough them with an M3 screw, and make sure that all the burrs come off.

Assemble the objective in the objective holder, the nut has RMS threads on it but it is unlikely that your printer can resolve them correctly, they will help guide the operation, but you will be actually threading the plastic with the metal of the objective. Do it nice and slow, and pay attention not to thread it in at an angle. If you have more than one objective, it mau be a good idea to print  multiple nuts and leave each objective on its own nut.

Test fit the eyepiece in  the optical tube, you can sand the inside or wrap some teflon tape around the eyepiece shaft to adjust the fit.

Apply a little bit of grease on the sloped sides of the collar of the spider, and insert the split ring on it.

Insert M3 nuts in the holes on the bottom side of the focusing knob, then slide it over the split ring (do this upside down, or the nuts will fall off!)
Do not glue the two parts together just yet, at the end of the assembling, after you check that all is ok, you can make this mating final by applying glue on the split ring (do not exagerate and be careful, you do not want any glue to end up between split ring and spider body).

Add some grease on the central and upper part of the optical tube, avoid greasing the extremity where the objective nut will be, it is ok if that is a bit stiffer, while all other rings have to turn as smooth as possible.

Insert the tube in the spider from below, rotating the focusing knob as soon as it catches the threads on the tube and draw it up. Be careful, the knob is not glued to the ring yet and there are no screws preventing the nuts to be dislodged if the two pieces separate.

Insert the springs in the holes on top of the knob, then add the anti backlash ring, tighten it down until it compresses the springs. A couple millimeters clearance should remain between the two rings, there are two sets of holes on the backlash ring so that you can adjust it in half a turn increments, you can change this later based on your preference.

Use M3x30 screws trough the backlash springs and down to the nuts in the fucus ring to secure the assembly together, do not overtighten the screws, and make sure the backlash ring is not tilted.

Test the assembly a few times, any stiffness should break in as the surfaces wear a little and the grease spreads.
If you are happy with the results, you can now push the optical tube up, this will detach the focus knob from the split ring, and you can add the glue and press it back down.   

>[!TIP] 
>You do not really need to glue the knob down, the microscope is actually perfectly useable also with the knob just pressed together, in use, you may occasionally experience it pushing up, but it is no big deal, so you can take your time testing, adding (or cleaning off) grease, etc... until you are happy.

Add the accessory ring on the top of the focus tube, followed by the eyepiece, and the objective ring on the bottom.

You can now install the asembly on the lower part of the microscope.

### Phone holder

Print the main body, and an insert to suit the clearance between the body and your specific eyepiece, the insert just slides in, and you can have more than one for different eyepieces. Install the phone holder by sliding it on the eyepiece, and use the accessory ring on the optical tube to move the support higher or lower based on the eye-relief distance of your eyepiece. 

If your holder wobbles because none of the pre-generated sleeves fits right on your eyepiece, you can use the source file in the [CAD](/CAD) folder to generate a custom size.

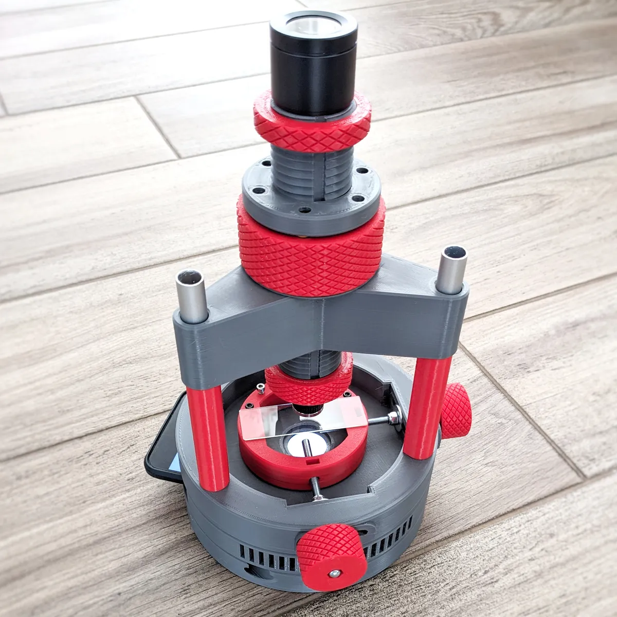
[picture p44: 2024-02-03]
Pictures/first_build.webp

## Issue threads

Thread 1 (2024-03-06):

### ISSUE TITLE
Fine Focus Spider Nacelle Tweak

### ISSUE THREAD

**Issue by irwtdvoys** [XVIIarcano/Galileo-Microscope#1]
The chamfer is missing from the bottom of two of the nacelle sliders. Caused a but of extra friction on mine until I cleaned it up.

![nacelle](https://github.com/XVIIarcano/Galileo-Microscope/assets/1695516/a9b71673-6daa-499b-b5de-0a6a70b321ad)

**Comment by XVIIarcano** [comment]
Ouch, I didn't notice this, not even when I printed the parts. I guess something in my specific prints (I don't remember if I have elephant foot compensation on or off for example) made it a bit more forgiving and mine did not get stuck.

Looking at the CAD file, this is a bit odd, because that chamfer should be the result of a single operation inf Fusion, pointed at the whole perimeter, I see now that for some reason it only produces the 1mm chamfer on one lobe, despite the others being identical all around. 

I can't screenshot while holding down CTRL, so here is a shot of the screen instead:
https://github.com/XVIIarcano/Galileo-Microscope/assets/131447789/13613849-8f98-47db-833a-8d518f26c60f

If I reduce the chamfer amount to 0.4 it manages to calculate the operation correctly. 
If I add a separate operation for the rest of the perimeter, it also works just fine.
Why all at once for 1mm is an issue is beyond my understanding...

I went for the separate 1mm operation and I have now updated the STLs and CAd files. 

Thanks a lot for pointing this out!

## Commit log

2024-01-21 Added RMS thread
2024-01-23 added finer pitch thread
2024-01-23 Create Microscope threads.xml
2024-01-23 Update Microscope threads.xml
2024-01-23 Create Objective nut.stl
    [Objective nut.stl]
2024-01-24 Create Optical Tube.stl
2024-01-24 published some STLs
    [Backlash ring.stl, Objective nut (1x objective).stl, Piston (x3).stl, Spider.stl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]
2024-01-24 published STLs
    [Accessory ring.stl, Focus knob.stl]
2024-01-25 added more stls
    [Cart.stl, Knob.stl, Piston (x3).stl, Spider.stl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]
2024-01-27 added STLs
    [BYO Illumination Module.stl, Base module.stl, Cover.stl]
2024-01-28 Updated STLs
    [Base module.stl, Ghetto_paper_diffuser.stl, Stage module.stl]
2024-01-28 updated stl
    [Pad (x3 - TPU).stl, Phone tray.stl, Stage module.stl, insert - 2mm.stl]
2024-01-28 updated instructions
    [insert - 2mm.stl]
2024-01-29 updated phone tray STLs
    [Insert 25.4 mm.stl, Insert 26.4 mm.stl, Insert 27.4 mm.stl, Insert 28.4 mm.stl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]
2024-01-29 added CAD files
    [Base module generator.f3d, Basic Elements Generator v3.f3d]
2024-01-29 added lots of stuff
    [Base module generator.f3d, Phone holder standoff accessory.stl, Standoff accessory ring.stl, Standoff with accessories v5.f3d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]
2024-01-30 Update Standoff with accessories v5.f3d
    [Standoff with accessories v5.f3d]
2024-01-31 major update ahead of release
    [Insert 25.4 mm.stl, Insert 26.4 mm.stl, Insert 27.4 mm.stl, Insert 28.4 mm.stl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]
2024-01-31 added JIS tube
2024-02-01 added fine focusing stage
    [Fine focus Knob.stl, Nachelle.stl, Rotor.stl, Spider body.stl]
2024-02-01 updated fine focuser mod
    [Spider body.stl]
2024-02-01 updated fine focus mod
    [Rotor.stl, Spider body.stl, Spring retainer (x3).stl]
2024-02-02 updated fine focus folder
    [Fine focus Knob.stl, Nachelle.stl, Rotor.stl, Spider body.stl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]
2024-02-02 updated fine focus
    [Nacelle PTFE.stl, Nacelle.stl, Nachelle.stl, Rotor.stl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]
2024-02-06 Renamed folder
    [Fine focus Knob.stl, Nacelle PTFE.stl, Nacelle.stl, Rotor.stl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]
2024-02-08 increased tolerances
    [Nacelle PTFE.stl, Nacelle.stl, Rotor.stl, Spider body.stl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]
2024-02-08 main update for the fine focuser
    [Nacelle PTFE.stl, Paper template.stl, Rotor.stl, Spider.stl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]
2024-02-09 Added base with drawers
    [Base module 30.stl, Base module 60.stl, Box large 30.stl, Box large 60.stl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]
2024-02-09 corrected orientation
    [Phone tray.stl]
2024-02-10 0.6 option for fine focuser and inital files for better stage
    [Knob lower (x2).stl, Knob upper (x2).stl, Lower backer (x2).stl, Lower plate.stl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]
2024-02-10 updated anti backlash
    [Knob lower (x2).stl, Knob upper (x2).stl, Module.stl]
2024-02-11 improved mechanism
    [Lower plate.stl, Module.stl, Upper plate.stl]
2024-02-11 corrected errors
    [Lower plate.stl, Module.stl]
2024-02-11 added fine movement stage
    [Fine Knob (x2).stl, Lower plate fine.stl, Module fine.stl]
2024-02-12 Update Knob upper (x2).stl
    [Knob upper (x2).stl]
2024-02-12 updated assembly instructions
    [Fine Knob (x2).stl]
2024-02-12 added plugs
    [Plug lower.stl, Plug upper.stl]
2024-02-12 Update Module fine.stl
    [Module fine.stl]
2024-02-12 reorganized folder
    [Fine Knob (x2).stl, Knob lower (x2).stl, Knob upper (x2).stl, Lower backer (x2).stl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]
2024-02-13 Update Fine Knob (x2).stl
    [Fine Knob (x2).stl]
2024-02-14 adjusted clearance of the fine gear
    [Lower plate fine.stl, Module fine.stl, Plug lower.stl, Plug upper.stl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]
2024-02-18 updated inserts and main readme
    [Insert 25.4 mm.stl, Insert 26.4 mm.stl, Insert 27.4 mm.stl, Insert 28.4 mm.stl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]
2024-02-20 Added turret
    [Hub.stl, Petal (x3).stl, Spring retainer.stl, ring nut.stl]
2024-02-23 Update Upper plate.stl
    [Upper plate.stl]
2024-03-06 fixed missing chamfers
    [Nacelle PTFE.stl, Nacelle.stl]
2024-03-16 micro 4/3 adapter
    [M43 adapter.stl, block.stl]
2024-03-17 corrected tube diameter
    [M43 adapter.stl, block.stl]
2024-04-09 Added Carry Case Files
2024-04-09 Create Filter Holder Files
2024-04-09 Created Filter Holder Files
2024-04-09 moved crayford in optical subfolder
    [Bearing_Block_x1.stl, Eyepiece_Adaptor_x1.stl, Focuser_Body_x1.stl, Tube_x1.stl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]
2024-04-09 reorganized folders
    [Base_x1.stl, Filter_Slider_Body_x1.stl, Lid_x1.stl, [a]_Clip_x4.stl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]
2024-04-09 Create Printing Instructions.md
2024-04-16 Update Assembly Guide.md
2024-04-16 Rename Focuser_Body_x1.stl to Focuser_Body_x1 (Built In removable support).stl
    [Focuser_Body_x1 (Built In removable support).stl, Focuser_Body_x1.stl]
2024-04-16 Rename Bearing_Block_x1.stl to Bearing_Block_x1 (Built In removable Support Version).stl
    [Bearing_Block_x1 (Built In removable Support Version).stl]
2024-04-16 Update and rename Bearing_Block_x1 (No Support).stl to Bearing_Block_x1 (No Support Version).stl
    [Bearing_Block_x1 (No Support Version).stl]
2024-04-16 Update Printing Instructions.md
2024-04-20 Initial upload of File
    Upload of files posted to Printable on 4/15/2024.
    [Bottom LED Lighting Module.stl, Top LED Holder.stl, Top LED Standoff Mount with stub.stl, Top Link A.stl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]
2024-04-20 moved LED mnod to subfolder
    [Bottom LED Lighting Module.stl, Top LED Holder.stl, Top LED Standoff Mount with stub.stl, Top Link A.stl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]
2024-06-03 added serial generator
    [Serial standoff generator.scad]
2024-07-22 made the tube thread tolerance parametric
2025-11-13 Added mods for focus knob and 30 mm tube
    [Accessorized Focus Knob.stl, Accessorized Split ring.stl, Lever.stl, galileo-30mm-eyepiece-tube.step]
2025-11-14 added screw lenght in readme
2025-11-14 Add cover STL
    Added turrett cover
    [Turrett cover.stl]
2025-11-14 Add fine focus knob and wheel STL files
    Added new 3D model files for the fine focus small knob and fine focus wheel in the Accessorized focus knob module.
    [Fine focus small knob.stl, Fine focus wheel.stl]
2025-11-15 Reoriented Turrett cover STL file
    [Turrett cover.stl]
2025-11-16 Update focus knob models and documentation
    [Accessorized Focus Knob.stl, Accessorized Split ring.stl, Fine focus small knob.stl, Fine focus wheel.stl]
2025-11-27 updated focus wheel files
    [Fine focus wheel.step, Fine focus wheel.stl]
